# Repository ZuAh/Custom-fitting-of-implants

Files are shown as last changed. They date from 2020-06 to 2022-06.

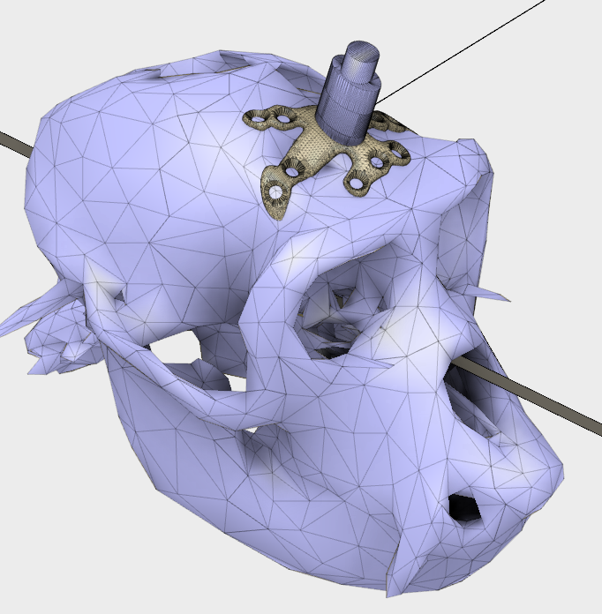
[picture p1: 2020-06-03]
02 template and example parts/parts responding to HP steps/01-SkullWithHP.PNG

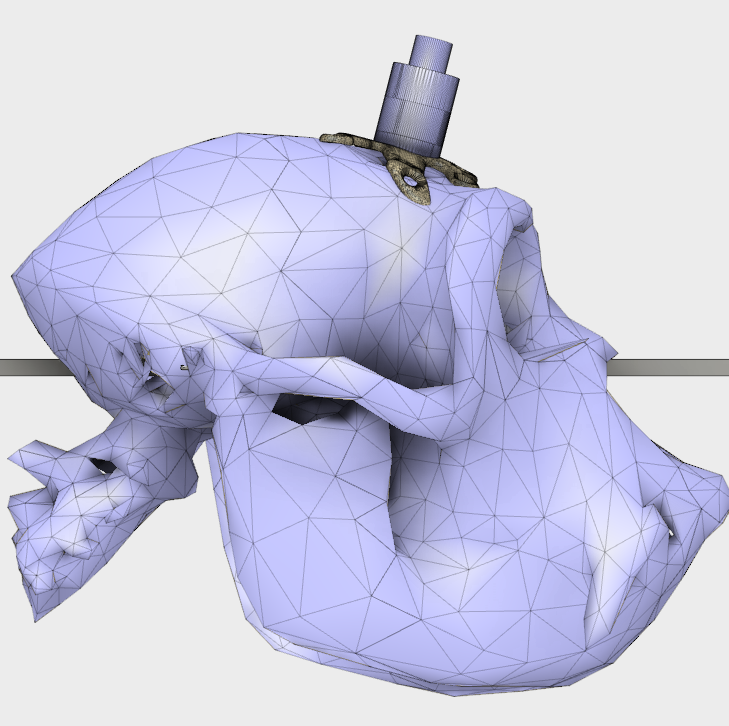
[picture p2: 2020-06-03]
02 template and example parts/parts responding to HP steps/02-SkullWithHP.PNG

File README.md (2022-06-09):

# Universal guide for skull extraction and custom-fitting of implants to continuous and discontinuous skulls

Intracranial neurophysiological recordings require chronic implants to provide transcranial access to the brain. Especially in larger animals, which participate in experiments over extended periods of time, implants should match the skull curvature to promote osseointegration and avoid tissue and bacterial ingress over time. Proposed CAD methods for designing implants to date have focused on naïve animals with continuous and even skull surfaces and calculate Boolean differences between implant and skull surface to fit the implant to the skull curvature. However, custom-fitting by calculating the difference fails, if a discontinuous skull surface needs to be matched. Also, the difference method does not allow designs with constant material thickness along the skull curvature, e.g. to allow fixed screw lengths. We present a universal step-by-step guide for custom-fitting implants which overcomes these limitations. It is suited for unusual skull conditions, like surface discontinuities or irregularities and includes virtual bending as a process to match skull surfaces while maintaining implant thickness. We demonstrate its applicability for a wide spectrum of scenarios, ranging from complex-shaped single-pieced implants to detailed multi-component implant systems built on even or discontinuous skull. The guide uses only a few software tools and the final virtual product can be manufactured using CNC milling or 3D printing. A detailed description of this process is available on GitHub including step-by-step video instructions suitable for users without any prior knowledge in CAD programming. We report the experience with these implants over several years in 11 rhesus monkeys.

This repository provides a detailed step-by-step tutorial to design and custom-fit implants. The main PDF document 'EDT_Tutorial_ReadMe' will guide you through the individual steps, which are completed by video tutorials indicated in red.

It is recommended to clone or download the entire repository to have best access to all materials.

Link to full paper on eNeuro: https://www.eneuro.org/content/early/2022/05/31/ENEURO.0028-22.2022 
Citation: DOI https://doi.org/10.1523/ENEURO.0028-22.2022

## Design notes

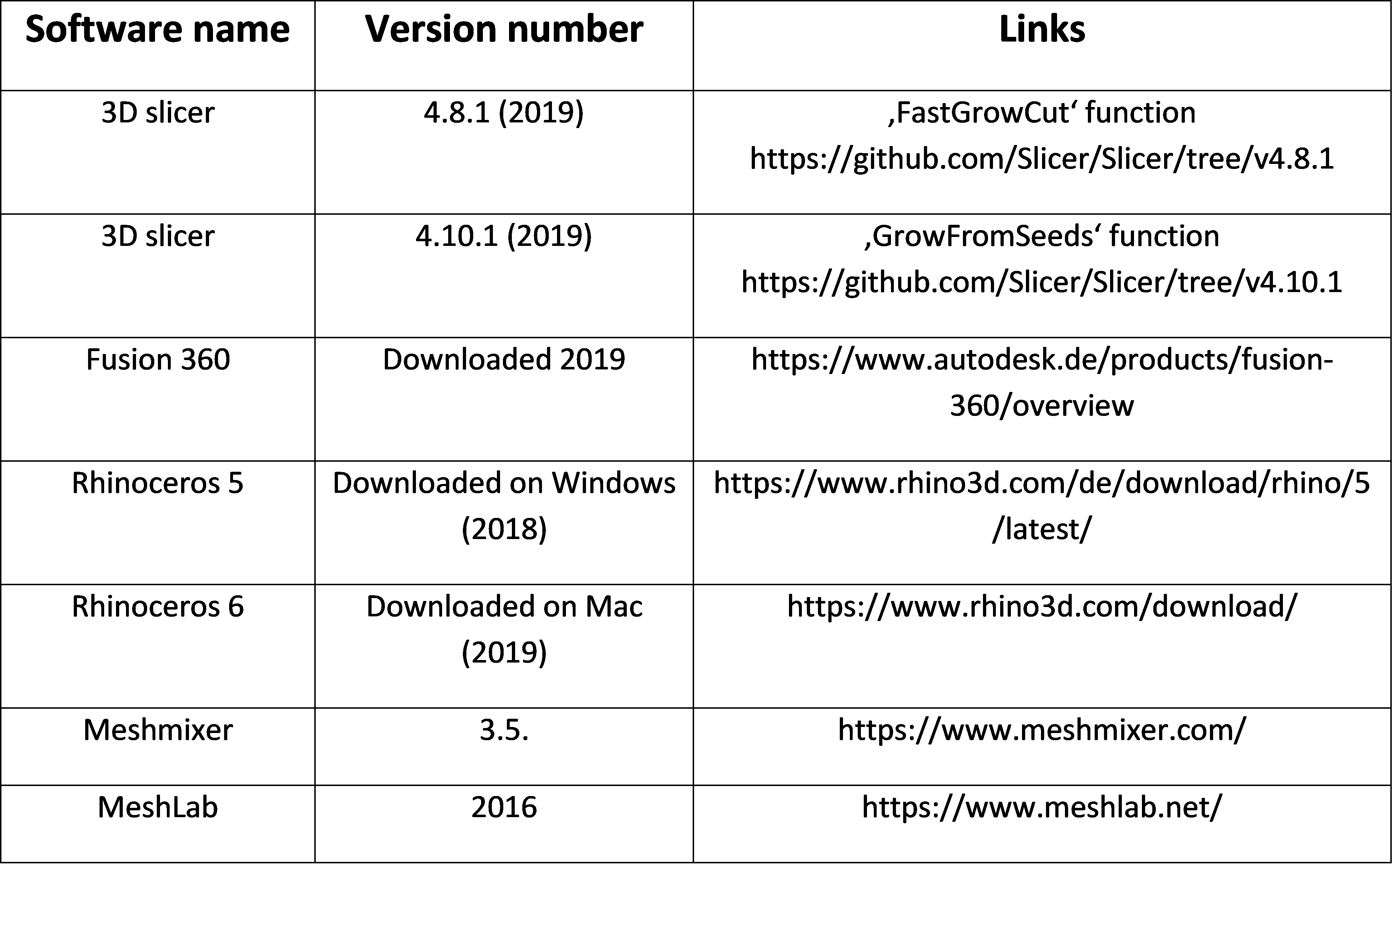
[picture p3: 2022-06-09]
Table1-1.tif

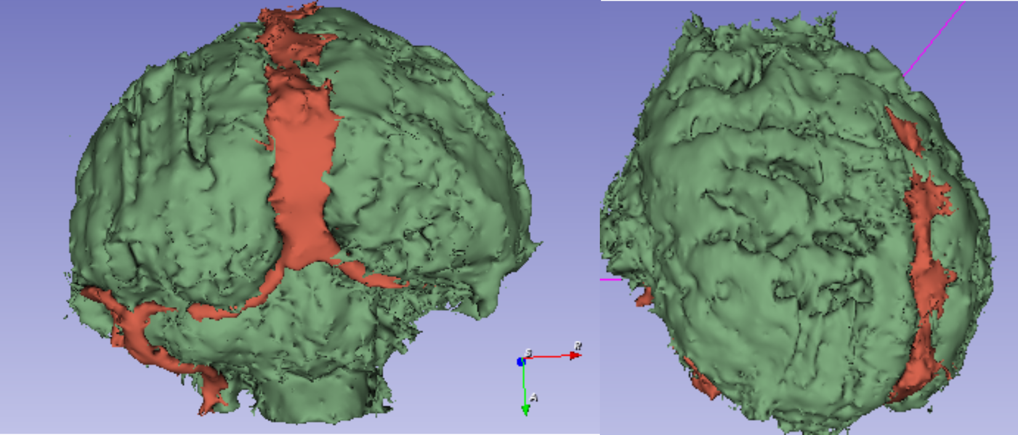
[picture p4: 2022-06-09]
Figure1-1.tiff

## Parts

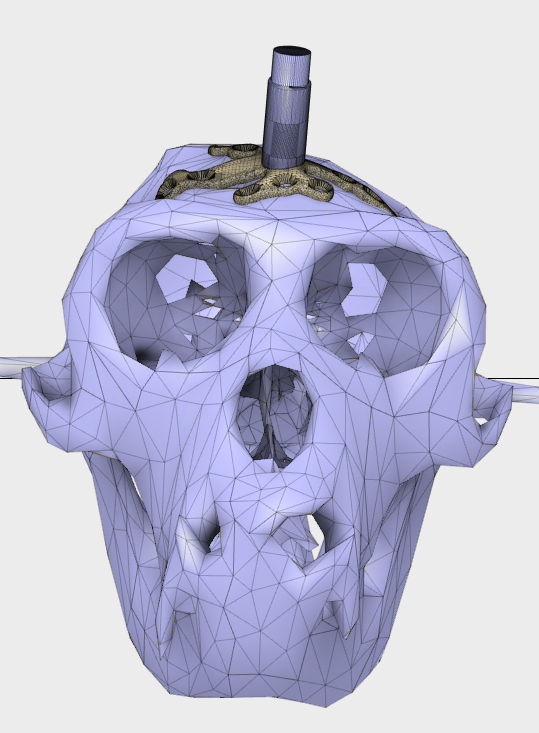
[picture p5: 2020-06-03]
02 template and example parts/parts responding to HP steps/03-SkullWithHP.PNG

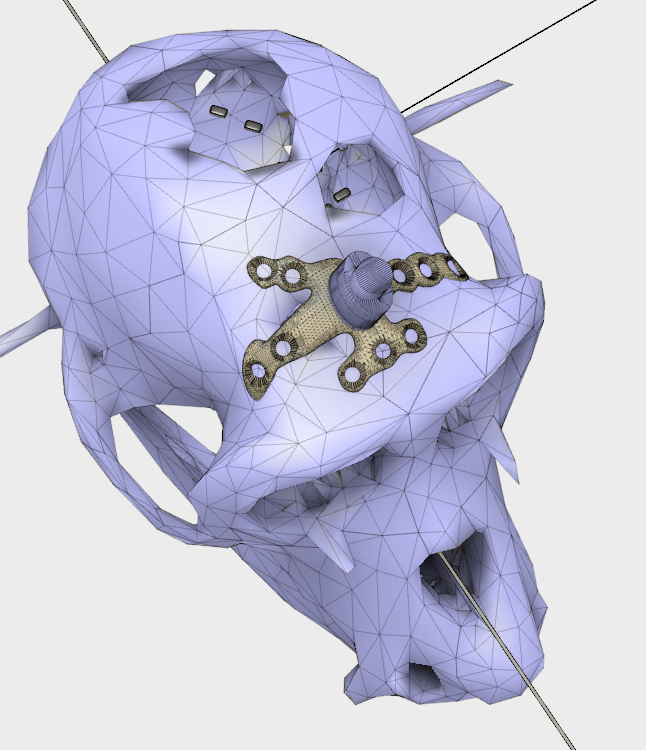
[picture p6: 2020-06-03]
02 template and example parts/parts responding to HP steps/04-SkullWithHP.PNG

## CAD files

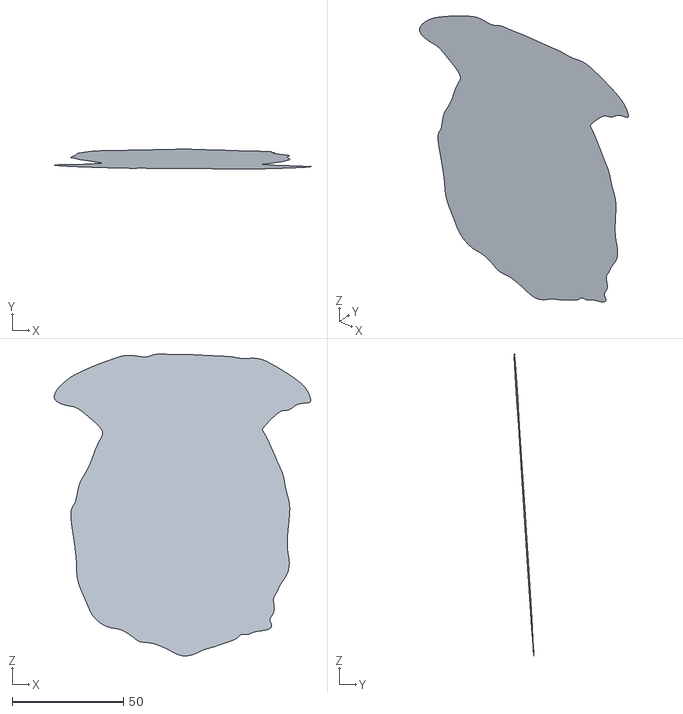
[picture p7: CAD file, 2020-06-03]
02 template and example parts/06-planarSkullSizeTemplate.stl
115.6 x 8.88 x 136.0

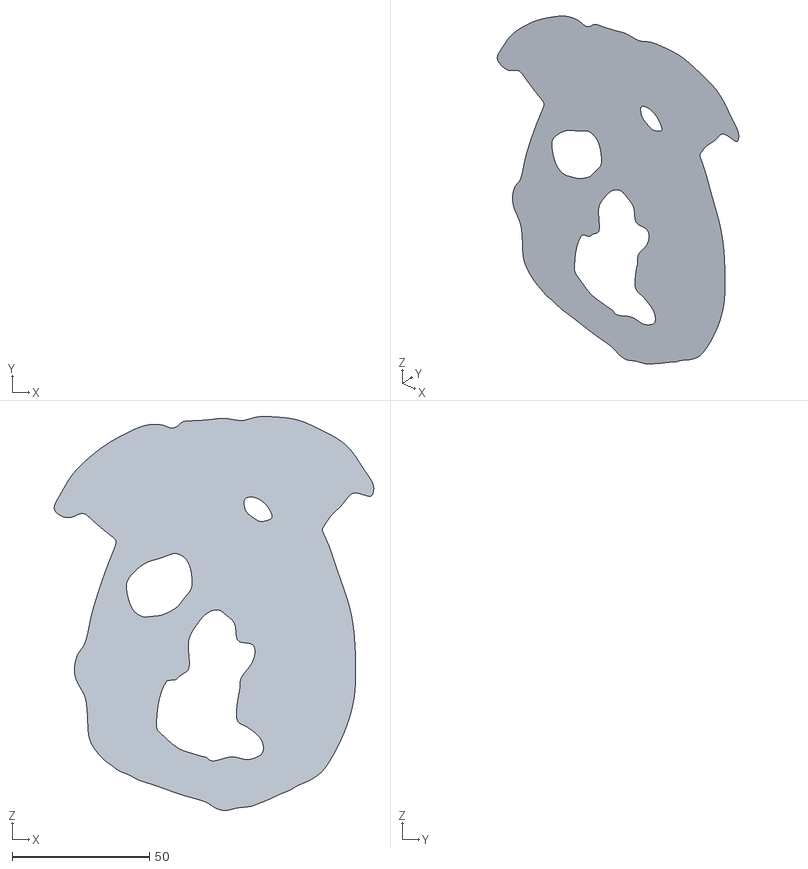
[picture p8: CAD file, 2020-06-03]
02 template and example parts/parts responding to HP steps/07-planarSkullRESIZED.stl
116.6 x 5.14e-15 x 143.7

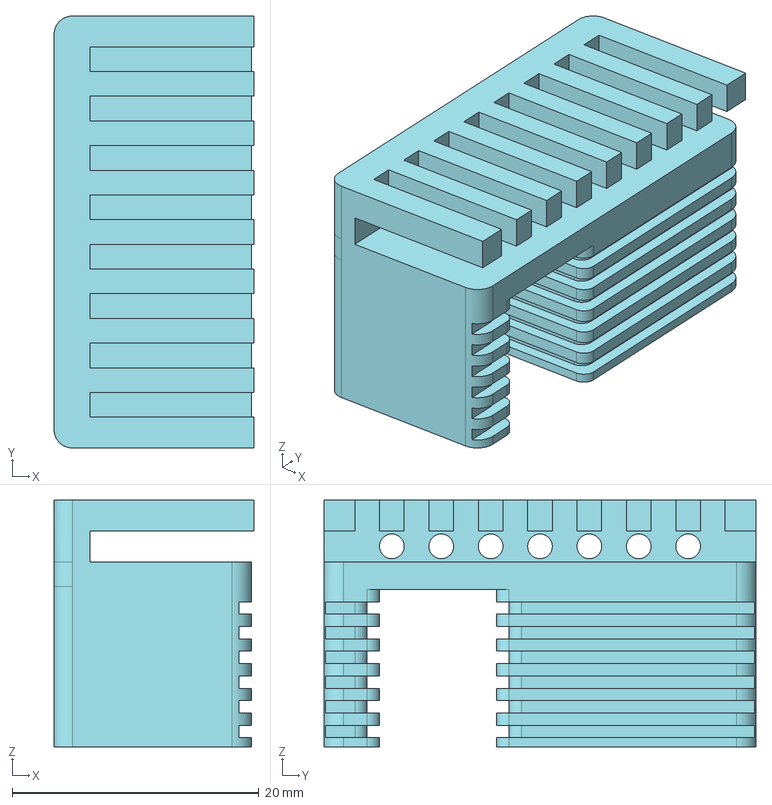
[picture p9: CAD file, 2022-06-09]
02 template and example parts/wireless chamber inlays/Arrayholder_unmolded.step
16.2 x 35.0 x 20.0 mm

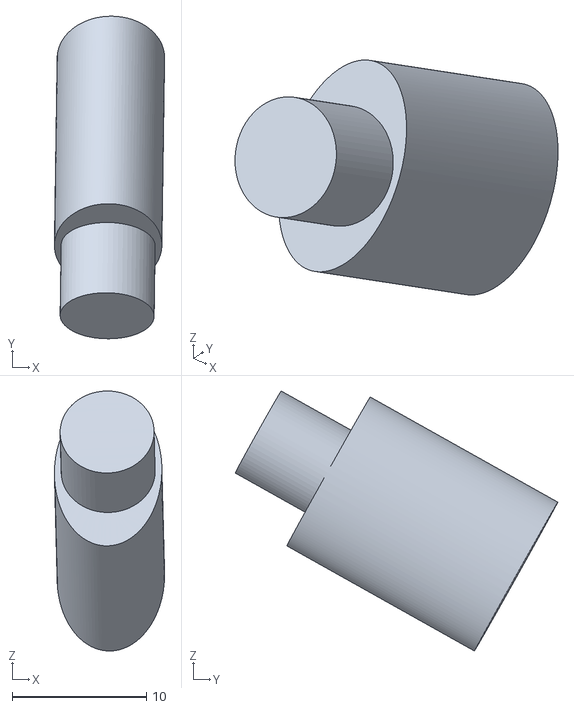
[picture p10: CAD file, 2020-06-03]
02 template and example parts/12-Cylinder_H.stl
8.20 x 24.0 x 19.3

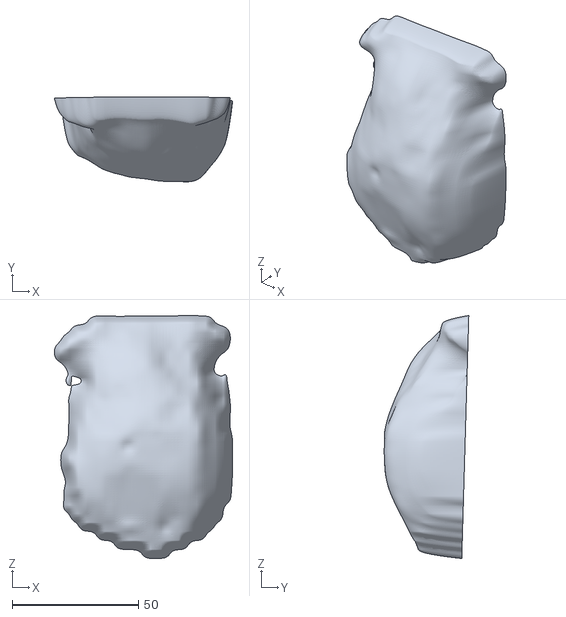
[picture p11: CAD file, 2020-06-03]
02 template and example parts/parts responding to HP steps/05-DrapeTrimmed.stl
70.6 x 33.5 x 96.1

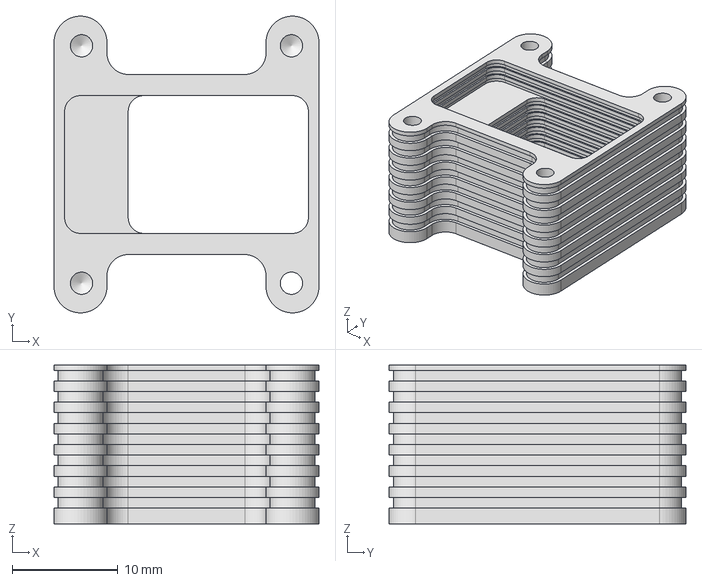
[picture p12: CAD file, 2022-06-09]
02 template and example parts/wireless chamber inlays/BoardHolder_unmolded.step
25.0 x 28.0 x 15.0 mm

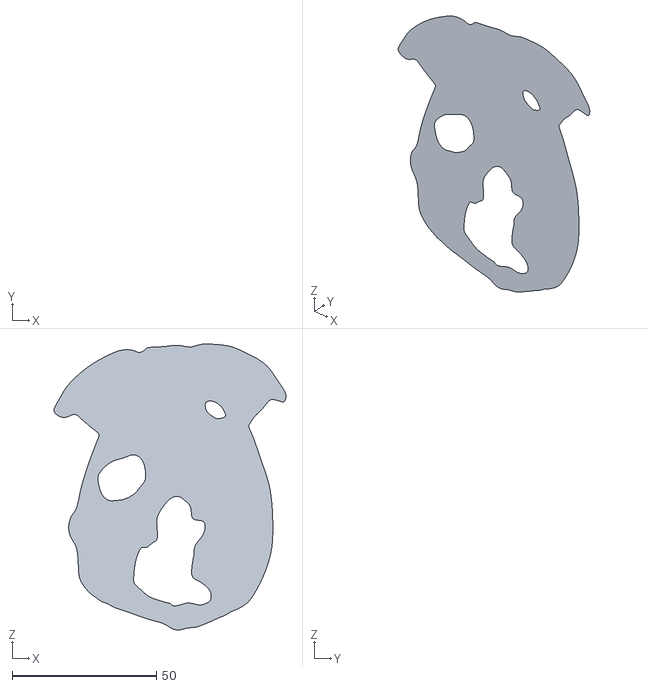
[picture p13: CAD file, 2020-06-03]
02 template and example parts/parts responding to HP steps/02-planarSkull.stl
80.5 x 3.55e-15 x 99.3

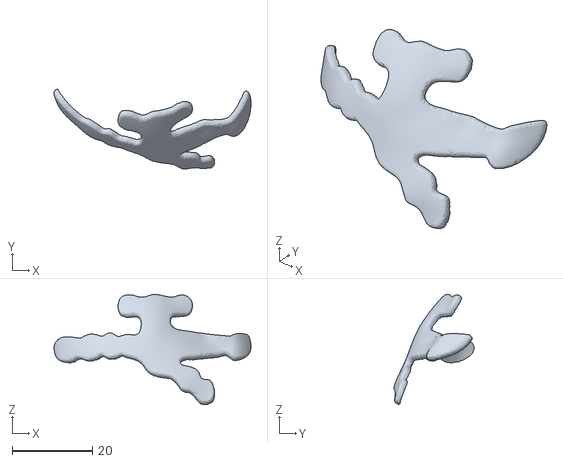
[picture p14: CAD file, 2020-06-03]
02 template and example parts/parts responding to HP steps/10-H_legsRaw.stl
49.2 x 20.0 x 27.6

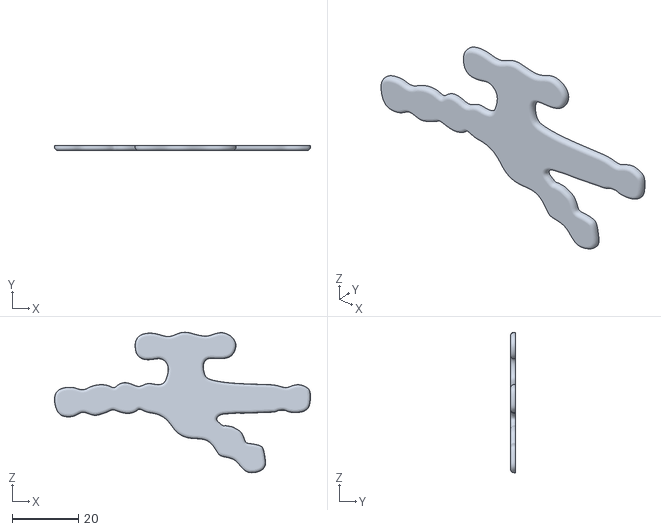
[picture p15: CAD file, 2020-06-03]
02 template and example parts/parts responding to HP steps/08-HPsurfaceFilletEdged.stl
77.5 x 1.50 x 42.5

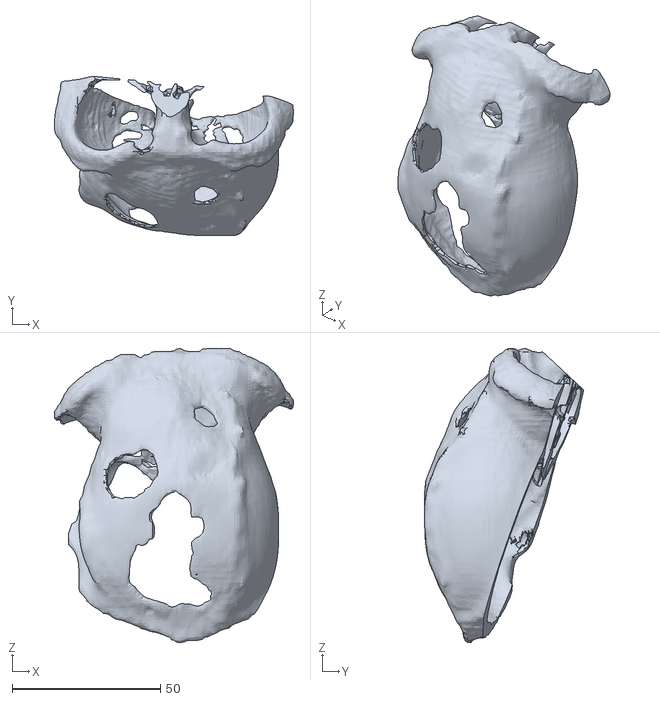
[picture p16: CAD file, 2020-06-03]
02 template and example parts/parts responding to HP steps/01-H_skull.stl
80.6 x 53.6 x 99.0

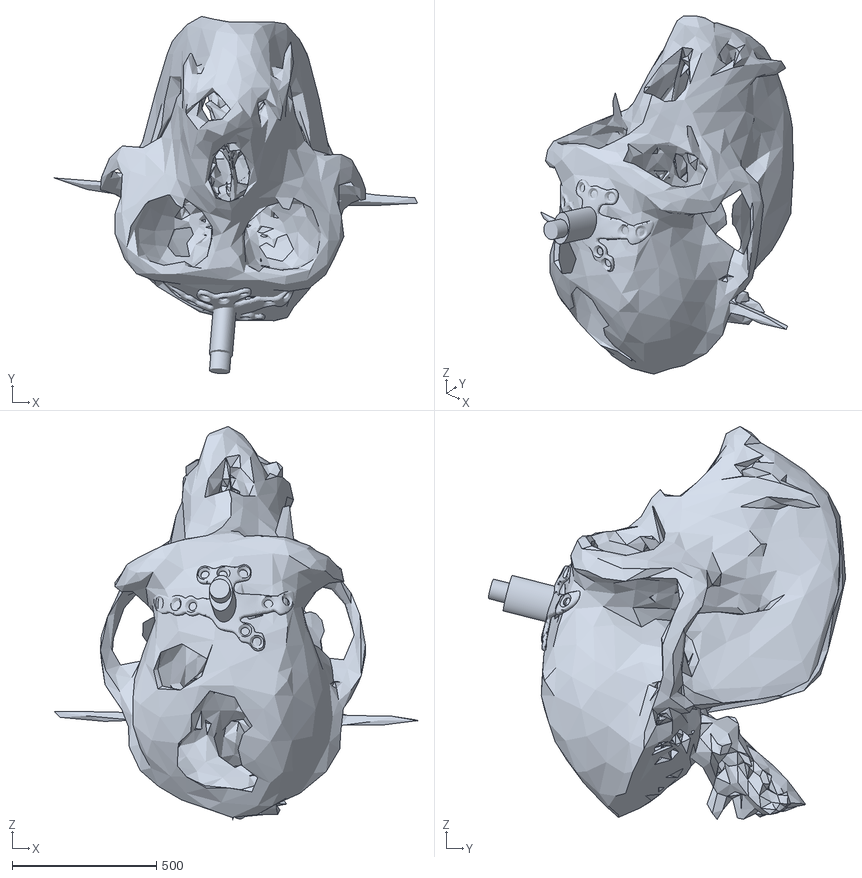
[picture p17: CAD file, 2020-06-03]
02 template and example parts/parts responding to HP steps/14-HPwithSkull.stl
1257.3 x 1237.3 x 1361.1

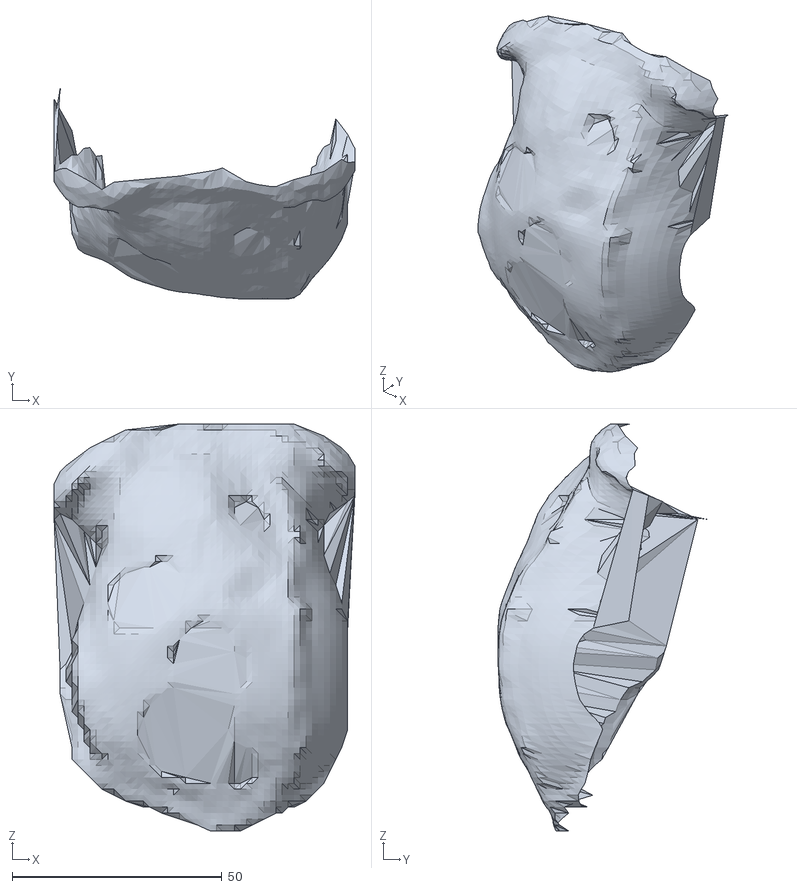
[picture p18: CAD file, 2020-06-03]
02 template and example parts/parts responding to HP steps/04-MeshPatch.stl
71.6 x 50.0 x 96.9

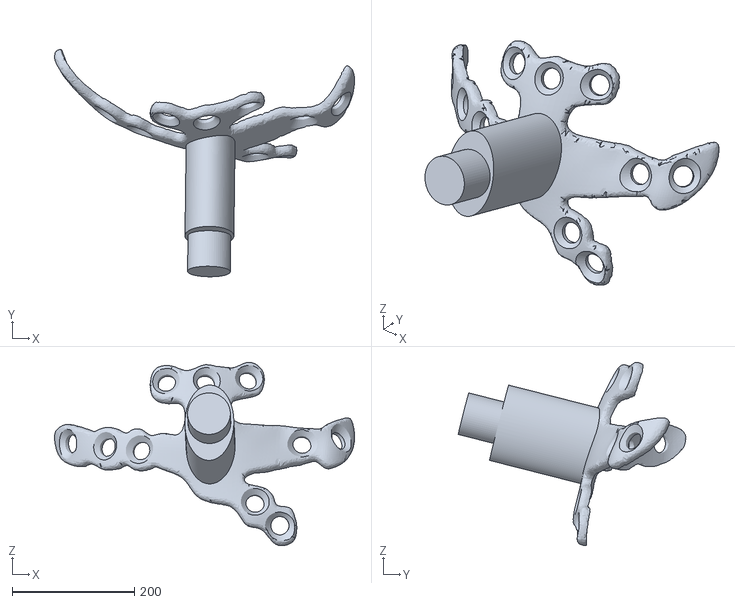
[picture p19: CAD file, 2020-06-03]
02 template and example parts/parts responding to HP steps/13-H_HP-final.stl
490.4 x 372.0 x 299.7

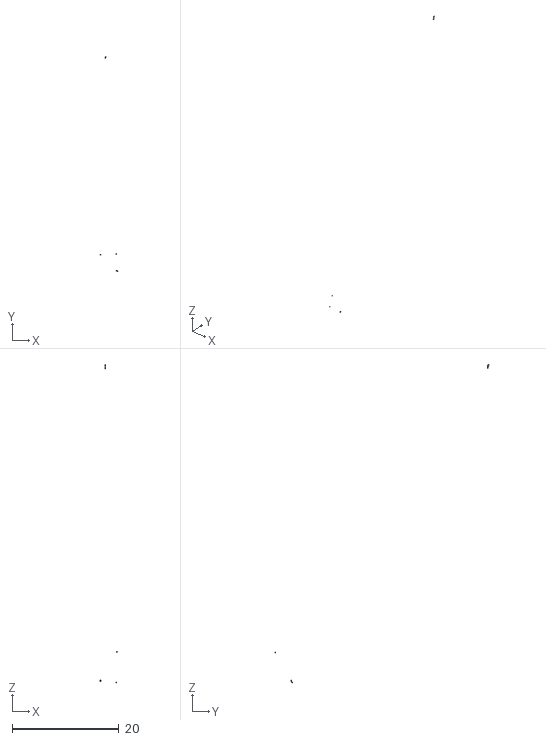
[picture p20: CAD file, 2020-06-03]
02 template and example parts/parts responding to HP steps/03-DrapePt.stl
3.20 x 40.0 x 59.5

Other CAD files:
02 template and example parts/parts responding to HP steps/11-H_HP-legs.stl

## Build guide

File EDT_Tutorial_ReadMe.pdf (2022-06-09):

Review version : Logo to be added upon acceptance

Version 08/20 | Page 1 of 16

## Universal guide for skull extraction and custom-fitting of implants to continuous and discontinuous skulls

## - TUTORIAL -

This tutorial describes how to customize and fit implants using Rhinoceros 6.0 and Fusion 360 (2018). Red numbers in brackets indicate the corresponding video tutorial, if available.

Description of how to reconstruct the 3D skull and brain as well the designing process of the unmolded chamber for wireless recordings can be found in form of video tutorials only and are not further explained.

Rhinoceros 6 -specific pointers:
- All commands can be entered in form of a text (type in command -> press enter)
- right mouse click repeats the last command used
- in quotation mark written words are the respective commands that can be typed in directly in the command line
- To move parts in space right click and drag. This is possible in all views except the “perspective” view. In the latter case press shift key + right click and drag.
- To rotate the view keep the right mouse button pressed while dragging in the “perspective” view

### Skull and brain extraction

[Step 0-1] Skull extraction using automatic threshold effect from a CT scan

[Step 0-2] Skull and/or brain extraction using automatic threshold effect from a MRI scan

[Step 0-3] Save and export the extracted 3D skull and/or brain model

### Preparatory Steps

[Step 1-1] Import the 3D skull model to Rhinoceros 6 (Rhino).

If your animal has an even skull, you can create the 3D reference surface directly (go to point 4 / [Step 3]). If the reconstructed skull contains uneven features, artefacts or holes, you need to patch up and remove them before continuing.

[Step 1-2] Remove unusual or uneven skull condition:
Generate curve points over the reconstructed 3D skull surface by entering the command “DrapePt”. A net of points is overlaid with the skull. Remove all points related to the uneven feature and create a newmesh with “MeshPatch”. Displace the original imported 3D skull.

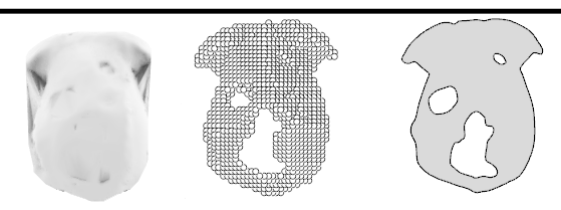
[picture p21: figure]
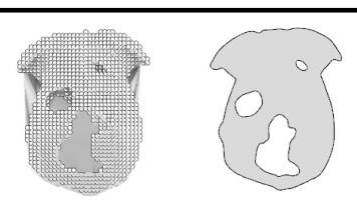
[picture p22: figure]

[Step 1-3] Create a 3D reference surface by using the command “Drape”.

DrapePt | MeshPatch

Trim all parts not needed by drawing a planar line, extruding ( “ExtrudeCrv”) and cutting (“Trim”) it.

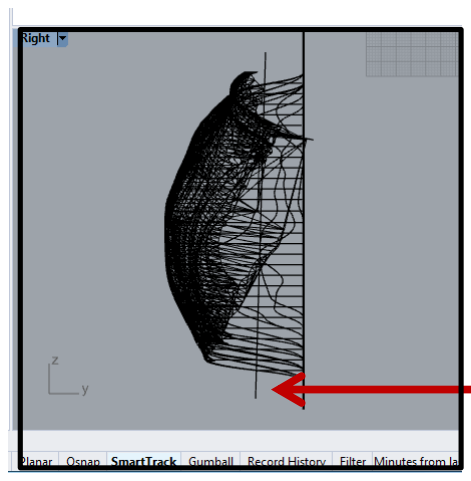
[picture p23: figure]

[Step1- 4] Create a 2D reference plane by using “Control Point Curve”. Make sure to draw the uneven features of your original skull reconstruction, if they are not artefacts and need to be integrated in the designing process (e.g. skull holes).

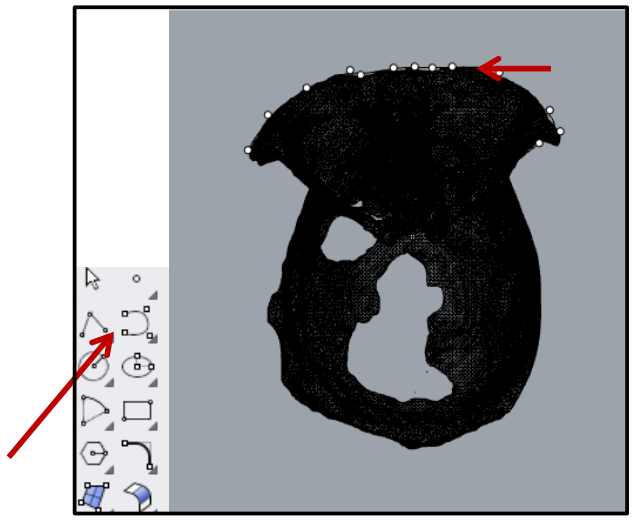
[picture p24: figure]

[Step 1-5] Extrude sketch by entering the command “PlanarSrf” Create holes in the 2D reference plane by using “MakeHole”.

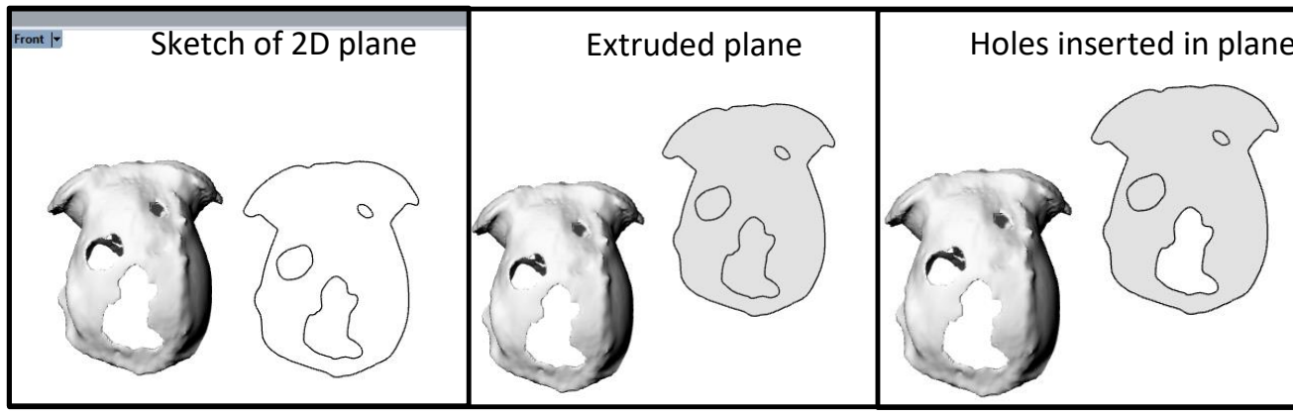
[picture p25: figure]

[Step 1-6] Scale the 2D reference plane so it matches the 2D reference plane (“Scale”). This plane is provided in the folder “parts_to work with”->06-planarSkullSizeTemplate” can be used as a size reference for an averaged sized male macaque skull.

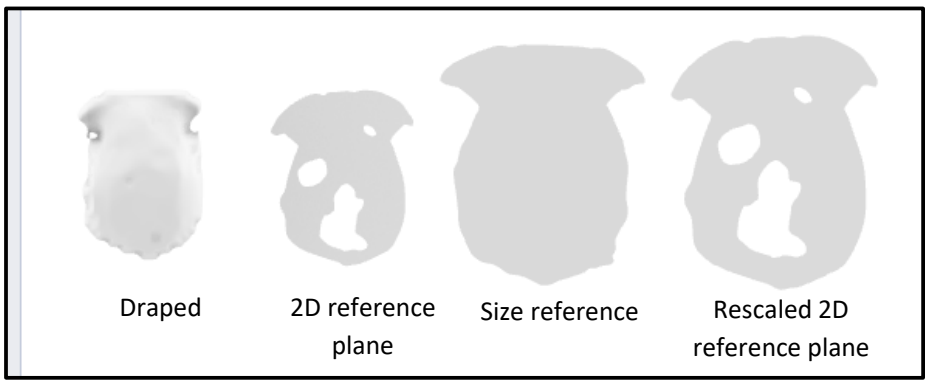
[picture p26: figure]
Draped; 2D reference; plane; Size reference; Rescaled 2D; reference plane

### Designing and fitting process - implants with maintained thickness (virtual bending)

[Step 1-7] To design implants where thickness after matching the skull curvature needs to be maintained, draw the sketch on the 2D reference plane (our lab: headposts and chambers’ legs width >7mm so M3 screws fit in).

Sketch of 2D plane | Extruded plane | Holes inserted in plane

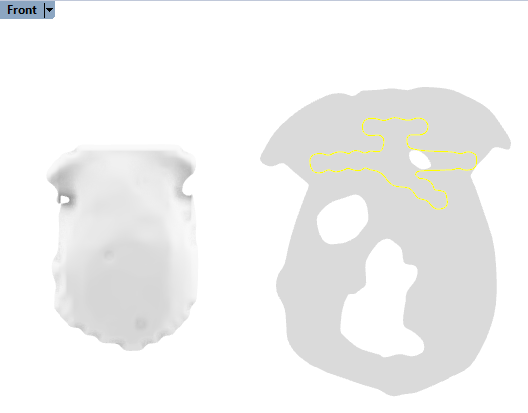
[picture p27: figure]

Extrude the sketch by using “ExtrudeCrv” to the thickness of your choice (our lab: 2mm). Make sure to create a “solid” extrusion (option during “ExtrudeCrv “ - command). Confirm the correct position of implant on the 2D reference plane and make sure that it is placed on top and not under the reference plane.

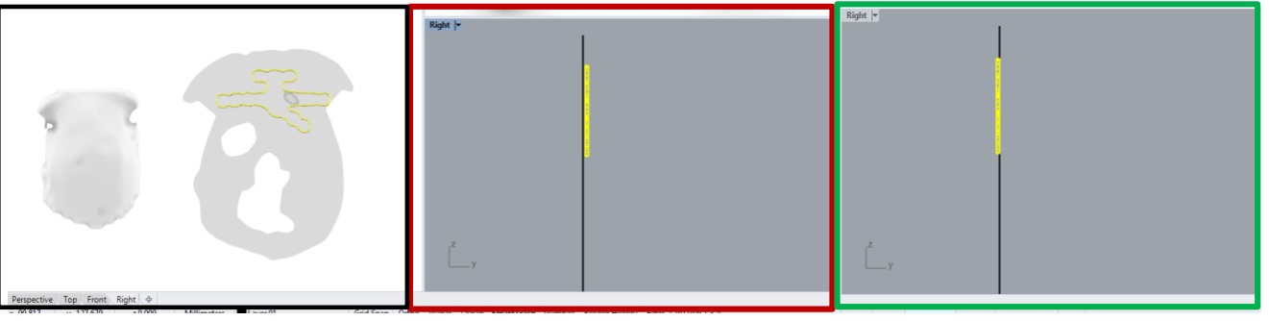
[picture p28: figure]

Smooth the edges of your extrusion (“FilletEdge”). This step needs to be performed before bending the legs to avoid problems in the next steps.

[Step 1-8] virtual bending
To mold the created part while maintaining a constant thickness use “FlowAlongSrf” and choose the 2D planar skull surface as the reference plane and the 3D skull surface as target. Check the result by placing it onto the original reconstructed skull.

[Step 1-9] When satisfied, this part can be modified further to create the required screw holes. These modifications can either be done in Rhino or in any other CAD software of your choice. To export for further use in a different CAD program, select the implant and export it in .STEP - format (File -> Export Selected).

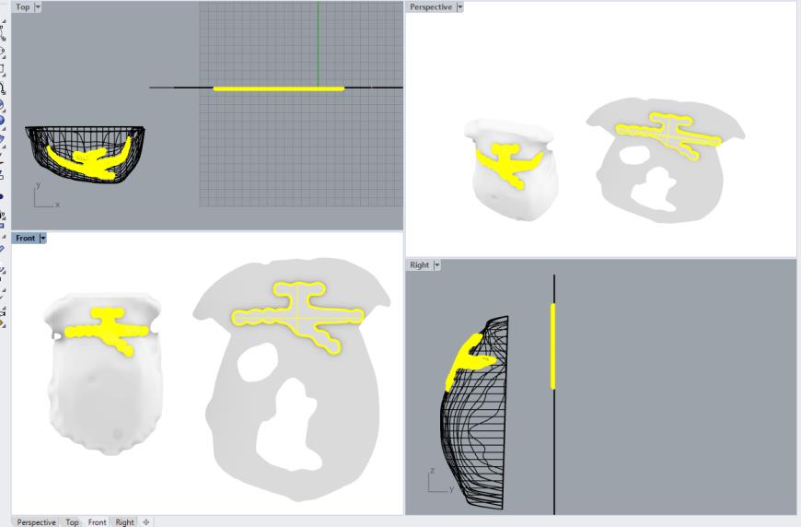
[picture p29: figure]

a. Create the screw holes.using Fusion
[Step 1-10] Import in Fusion 360 and rescale the model (factor 0.1) as Fusion downscales imported models by default.

[Step 1-11 - create screw holes using Fusion] The screw holes are created by drawing circular holes placed on the implant surface which are then extruded with the option "cut".
Measurement summary of our lab:
Screw holes: diameter 3 mm, extrude and cut 0.6 mm depth with taper angle 0° diameter 3 mm, extrude and cut by 1.00 mm with taper angle 45°
b. Or using Rhinoceros
[Step1- 11- create screw holes using Rhino] Use the command “RoundHole” and select the legs as the target surface. Select the suitable depth and radius for the holes and make sure to set the directions options to “SrfNormal”. You can create all holes in the same process. When finished, press enter. To create a taper angle use “ChamferEdge” and set the width (our lab: 1mm). Export implant in the file format suited for the manufacturing process of your choice.

[Step 1- 12] Place top part of implant.
For completion purposes the ellipsoid and cylinder measurements of the headpost’s top part are given. If you want to use the standard of our lab, you can simply import the file “12-Clyinder_H” and place it on top of the legs.

Ellipsoid: length 12.7 mm, width 8.00 mm, extrusion 14.00 mm
Top Cylinder: diameter 6.80 mm, extrusion 6.00 mm

Make sure to angle and rotate the top part so it’s perpendicular to your skull and not tilted.

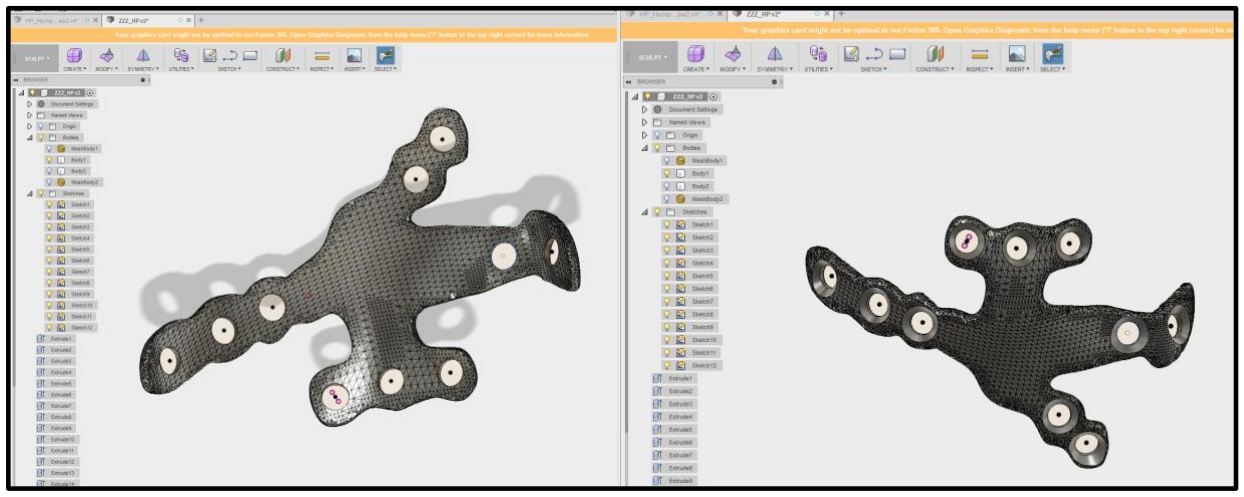
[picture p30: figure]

[Step 1-13] Convert the implant from “brep” to “mesh” and export implant in the file format suited for the manufacturing process of your choice. It is recommended to use .STL for 3D printing and .STEP for CNC milling.

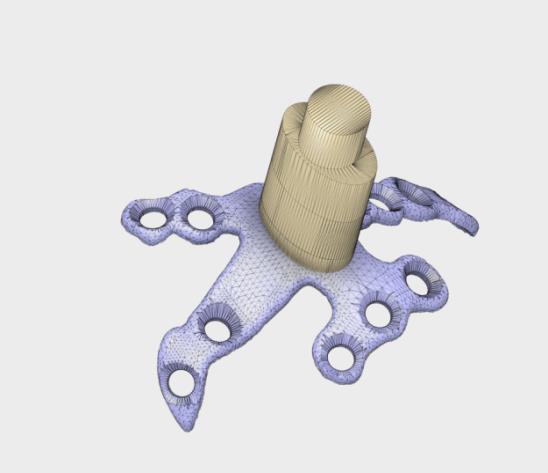
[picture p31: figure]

[Step 1- 14] Verify fit and location of implant by placing it on the original extracted 3D skull.

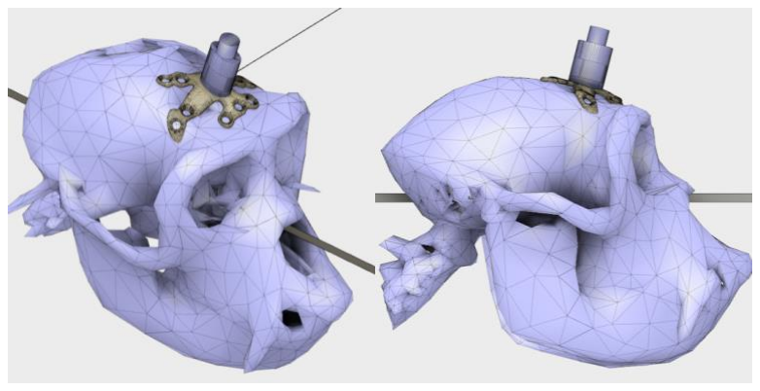
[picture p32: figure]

Headpost designed for an even, smooth skull of a naïve animal.

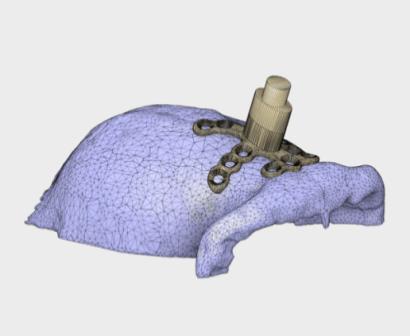
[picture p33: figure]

### Designing and fitting process - broad-spread implants without maintaining the thickness (virtual cutting)

Implants that extend over a large part of the skull and do not require to maintain their thickness are fitted as explained in the following.

As an example for this type of implant we will show how to design and fit a chamber for wireless recordings. Again, all designing steps can be done in Rhino or any other CAD program of your choice, experience and convenience.

Details about the designing can be found in these video tutorials:

[Step 2-1] Design the main body https://knowledge.autodesk.com/community/screencast/e2d2ce50-7afa-4d00-a959-b472e75504fd

[Step 2-2a] Create eyelets https://knowledge.autodesk.com/community/screencast/f108f929-814f-4b80-88d4-f1173e3b126e

[Step 2-2b] Alternative way of creating eyelets.
Draw two circles on the implant wall with the diameters 6 and 5 mm. Extrude by lofting (Create -> Loft).

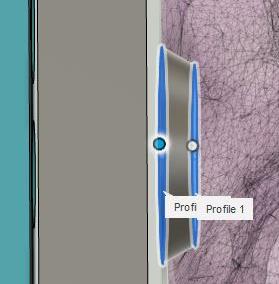
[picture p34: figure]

Create a sphere on the surface, which has the diameter 5mm. The sphere should have a radius of 5mm. Cut one half of the sphere by extruding the inner surface.

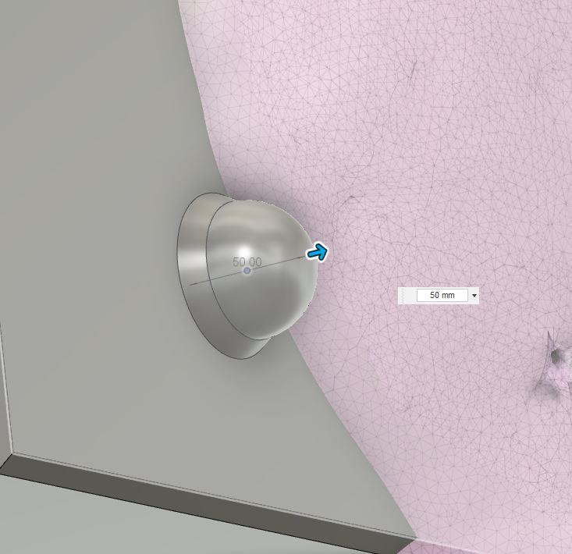
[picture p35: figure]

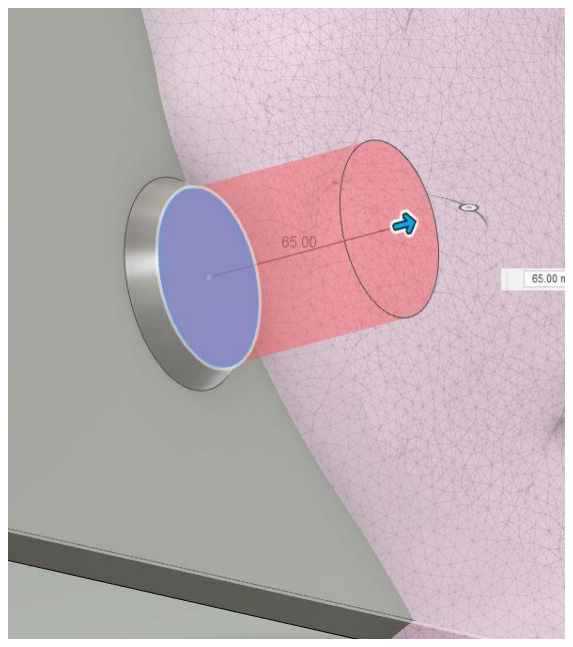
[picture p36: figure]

Rotate the Sphere by 180 degrees and create a distance between the cut sphere and the inner surface by 0.5mm.

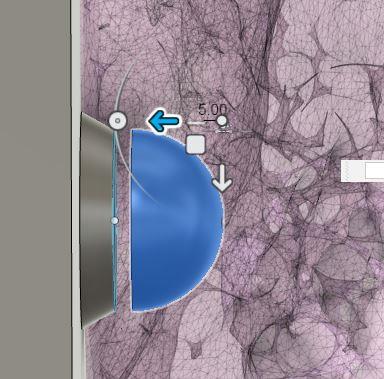
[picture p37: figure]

Bridge the gap by creating a Loft.

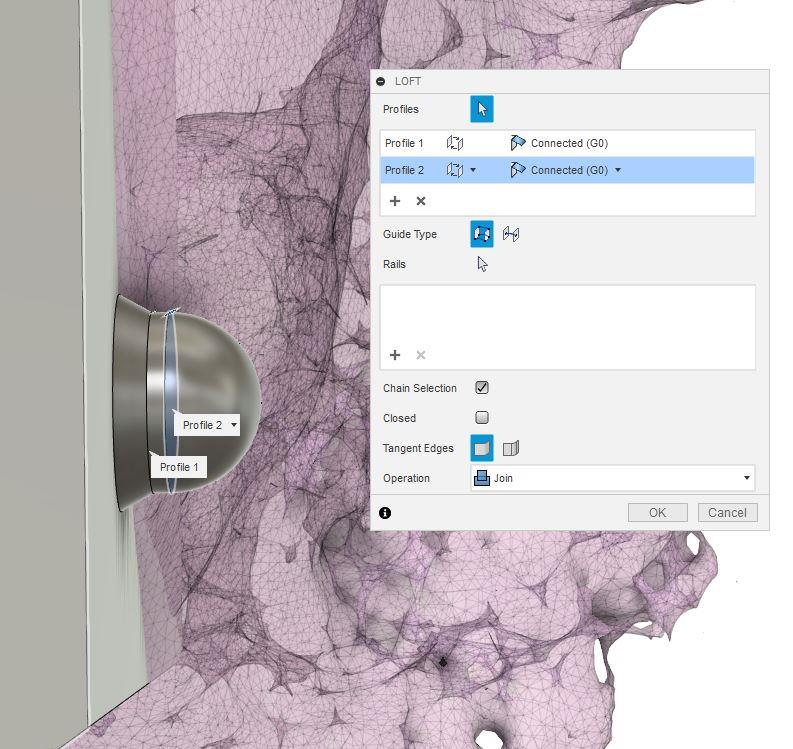
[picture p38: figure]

[Step 2-3] How to make a hole through the eyelet of the implant: https://knowledge.autodesk.com/community/screencast/95b632af-a998-497e-ab5f-031518697e4e

[Step 2-4] Before fitting, a 2D and 3D reference plane and surface need to be created (see Preparation). If not designed in Rhino, import the raw (not molded) chamber and all its parts in Rhino after saving them in .IGES. ‘Join’ all parts.

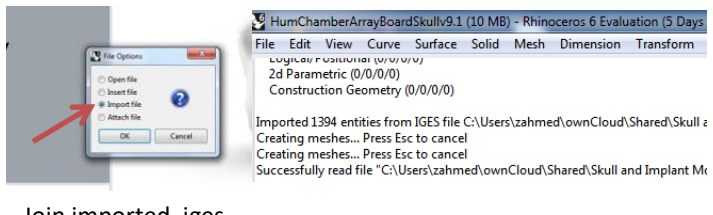
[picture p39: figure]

[Step 2-5] Place the implant on the 3D reference skull and push it through till an intersection is created between the raw chamber and the 3D skull surface.

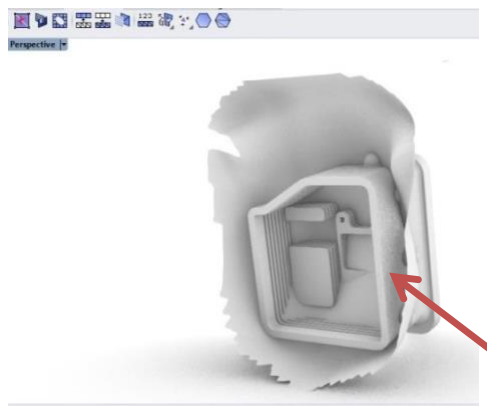
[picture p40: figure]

[Step 2-6] For fitting this type of implants use “BooleanDifference”. Detailed description shown in [Step 15 - create chamber top]

Import to Rhino

Join imported .iges

Export the fitted and customized implant in .STP format for CNC milling or importing to other CAD software. Use .STL for 3D printing.

[Step 2-7] Design furrows (can be designed before or after virtual cutting)..
Select inner side walls on which you want to create furrows. Press “Project” (key: P) to create a projection plane onto the wall.
Now draw rectangles that can be extruded into furrows.

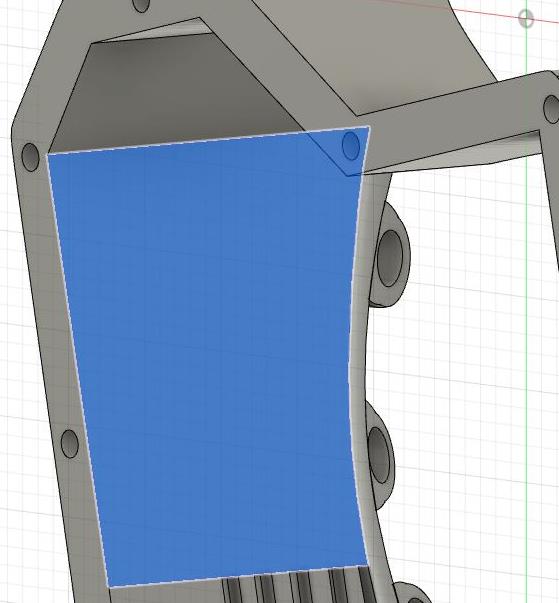
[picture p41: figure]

Select the rectangles and extrude to 1mm to create the furrows.

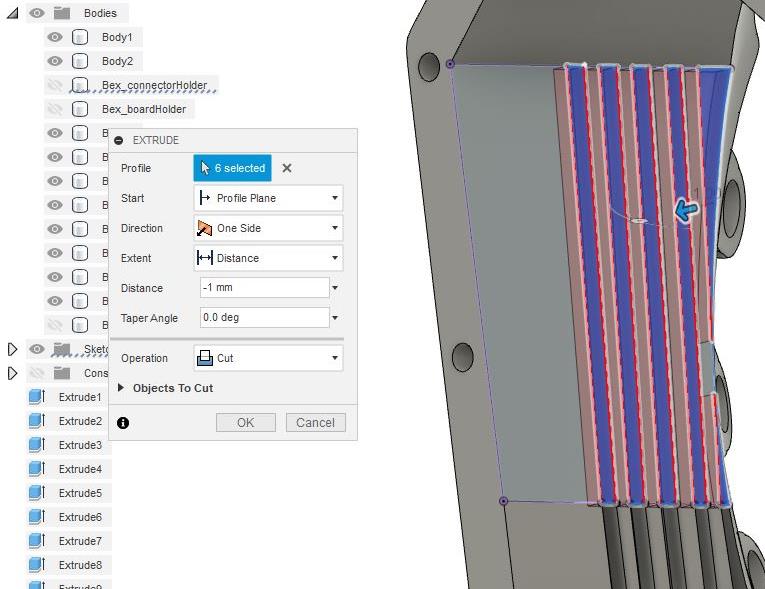
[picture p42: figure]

### Designing and fitting process - Hybrids

Implants requiring a mixture of both methods can be created as well.

In our example we show how to create a standard chamber.
This type of implant consists of legs, which should maintain their thickness for better osseintegration and a body which allows access to the craniotomy. This body does not need to maintain the same thickness but has to only follow the skull curvature.

For designing the legs the same procedure as described in “Designing and fitting process - implants with maintained thickness“ is used.

[Step 3-1] The basis of the top part is a cylinder (command “Cylinder”) that is created on top of the bottom part (here legs). Set the diameter and the height to your choice (our lab: diameter 24mm, end of cylinder 30mm).
Tilt and move till the top part is properly oriented and angled.
Pull the top part through both - the bottom part and the 3D skull surface - to generate an intersection. Create access to the craniotomy with “RoundHole” and select the cylinder as the “target surface”. To cut through the bottom part of the implant use “RoundHole” again but set direction to “Pick” (instead of “SrfNormal”).

[Step 3-2]

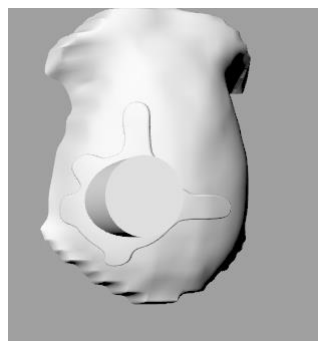
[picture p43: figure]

The top part of the chamber can be fitted to the skull curvature by using the “BooleanDifference” (for details see “Designing and fitting process - broad spread implants without maintaining the thickness”).

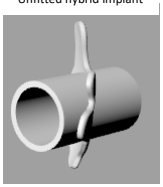
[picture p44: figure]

[Step 3-3] As the last step push the molded top part through the legs till around 1mm is sticks out on the other side. This allows a better fit to the craniotomy during surgery.

Create cylindric
top part

Create hole in
the chamber

Create access to
the craniotomy
Unfitted hybrid implant | Matched skull curvature

Export the implant in the appropriate file format. We recommend to use .STL for 3D printing and .STEP for CNC milling.

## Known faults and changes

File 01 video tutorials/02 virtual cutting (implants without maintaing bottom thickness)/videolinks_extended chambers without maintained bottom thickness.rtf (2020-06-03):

First, make an implant: https://knowledge.autodesk.com/community/screencast/e2d2ce50-7afa-4d00-a959-b472e75504fd
Second, make a screw attachment arm: https://knowledge.autodesk.com/community/screencast/f108f929-814f-4b80-88d4-f1173e3b126e
(Optional) Third, make a hole through the attachment arm and sphere: https://knowledge.autodesk.com/community/screencast/95b632af-a998-497e-ab5f-031518697e4e
